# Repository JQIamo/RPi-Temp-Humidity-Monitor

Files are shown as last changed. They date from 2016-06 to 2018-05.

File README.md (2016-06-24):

# RPi-Temp-Humidity-Monitor
Raspberry-Pi driven temperature and humidity sensing via DHT22.

Short-URL: http://git.io/vRFkn

## Ordering Boards:
v1.1 Boards are orderable from OSHPark at the following links:

- [PiTempLoggerv1.1-PiSide](https://oshpark.com/shared_projects/A5WHpdao) @ $34.50 per 3 boards
- [PiTempLoggerv1.1-Sensor](https://oshpark.com/shared_projects/NIQoCTse) @ $12.00 per 3 boards

They have been prototyped on a local board-fab machine, and a first run is en-route to the JQI.

## Other needed parts:
For one sensor baord:
- 1 DHT22 [from Adafruit?](https://www.adafruit.com/product/385)
- 1 of the above PiTempLoggerv1.1-Sensor
- 1 of 1-10k 1206 SMT resistor (use a lower resistance, e.g. 1-2k, if your ethernet cable is over 15 feet)
- 1 of 100nf 1206 SMT capacitor
- 1 of ethernet jack (Man. Part No. 555164-1, TE/Amp, get from any distributor)
- 1 Ethernet cable to connect to RPi (whatever length you need)

Per pi:
- 1 of the above PiTempLoggerv1.1-PiSide
- 8 of ethernet jack (Man. Part No. 555164-1, TE/Amp, get from any distributor)
- 1 of 26-pin 2x13 header
- 1 ribbon cable, either:
  - 26 pin
  - 40 pin
  - "Downgrade" cable [from Adafruit](https://www.adafruit.com/products/1986) <-Could also be made yourself with ribbon or connector
- 1 ethernet cable for network access

## Installing on a Raspberry Pi
See instructions in `INSTALL.md`

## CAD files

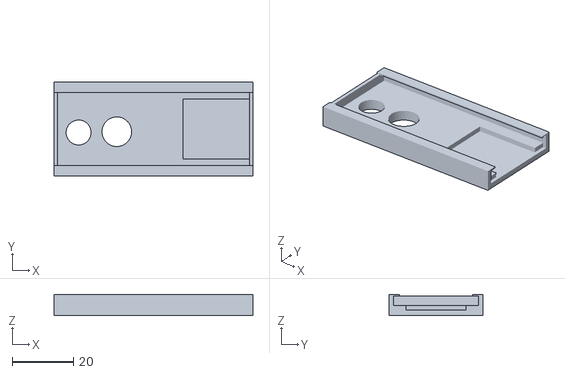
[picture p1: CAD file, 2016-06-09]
RPi-Tempmonitorcase.STL
64.8 x 30.7 x 6.86

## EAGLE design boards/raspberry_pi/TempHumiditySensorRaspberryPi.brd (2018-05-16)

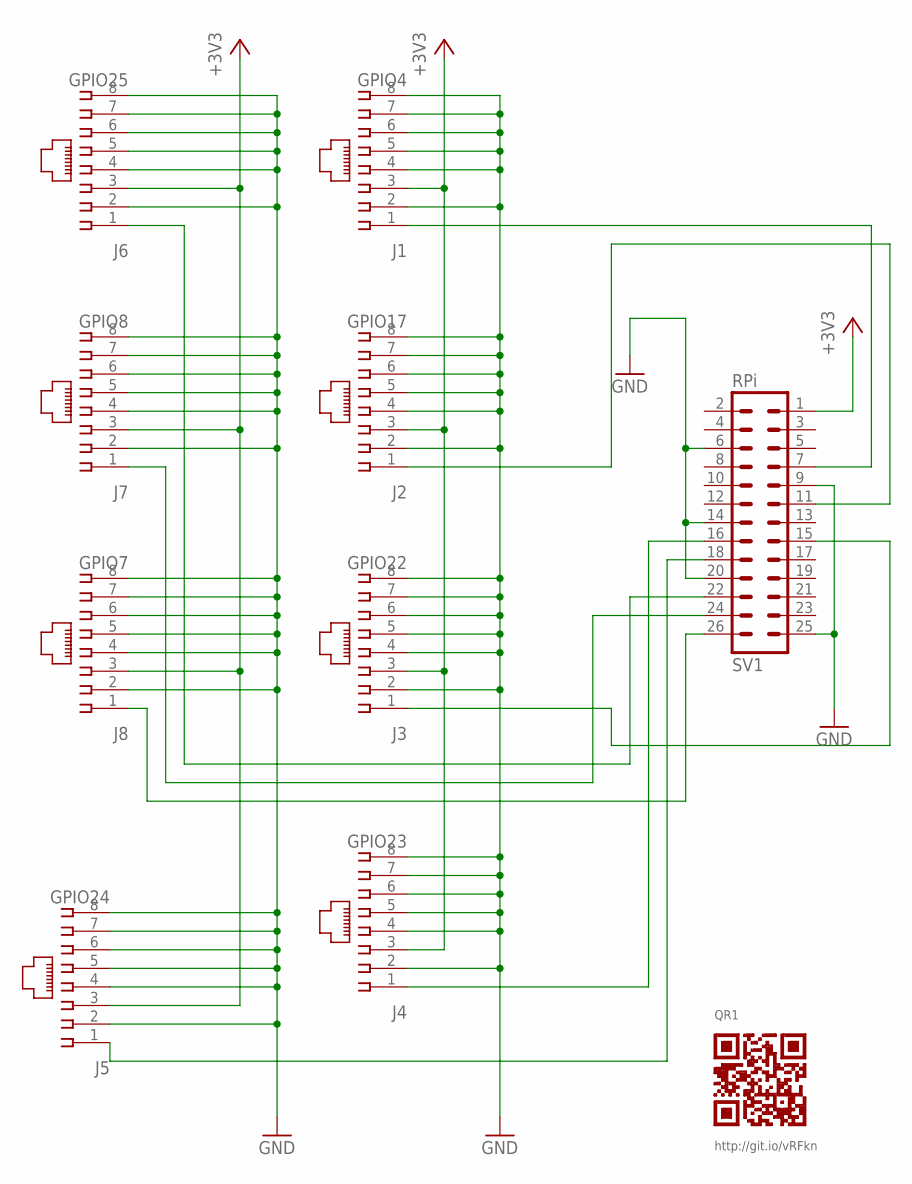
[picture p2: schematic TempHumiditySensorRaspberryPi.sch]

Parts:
J1: GPIO4; 555164-1; PARTNO 5555164-1
J2: GPIO17; 555164-1; PARTNO 5555164-1
J3: GPIO22; 555164-1; PARTNO 5555164-1
J4: GPIO23; 555164-1; PARTNO 5555164-1
J5: GPIO24; 555164-1; PARTNO 5555164-1
J6: GPIO25; 555164-1; PARTNO 5555164-1
J7: GPIO8; 555164-1; PARTNO 5555164-1
J8: GPIO7; 555164-1; PARTNO 5555164-1
QR1: QR-HTTP://GIT.IO/VRFKN
SV1: RPi; ML26; PARTNO SBH11-PBPC-D13-ST-BK

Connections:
+3V3: J1.3, J2.3, J3.3, J4.3, J5.3, J6.3, J7.3, J8.3, SV1.1
GND: J1.2, J1.4, J1.5, J1.6, J1.7, J1.8, J2.2, J2.4, J2.5, J2.6, J2.7, J2.8, J3.2, J3.4, J3.5, J3.6, J3.7, J3.8, J4.2, J4.4, J4.5, J4.6, J4.7, J4.8, J5.2, J5.4, J5.5, J5.6, J5.7, J5.8, J6.2, J6.4, J6.5, J6.6, J6.7, J6.8, J7.2, J7.4, J7.5, J7.6, J7.7, J7.8, J8.2, J8.4, J8.5, J8.6, J8.7, J8.8, SV1.6, SV1.9, SV1.14, SV1.20, SV1.25
unnamed: J1.1, SV1.7
unnamed: J8.1, SV1.26
unnamed: J2.1, SV1.11
unnamed: J3.1, SV1.15
unnamed: J4.1, SV1.16
unnamed: J6.1, SV1.22
unnamed: J7.1, SV1.24
unnamed: J5.1, SV1.18

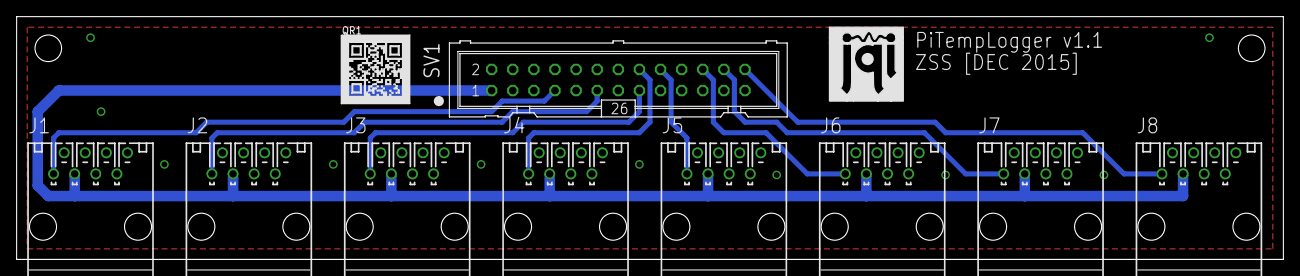
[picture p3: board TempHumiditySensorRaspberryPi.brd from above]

Board: 2 copper layers, 152.4 x 29.2 mm, 11 parts (0 on the bottom side), 10 nets.

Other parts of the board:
LOGO1: JQI-LOGOSILK; JQI_LOGO_NEGATIVE-SILKSCREEN

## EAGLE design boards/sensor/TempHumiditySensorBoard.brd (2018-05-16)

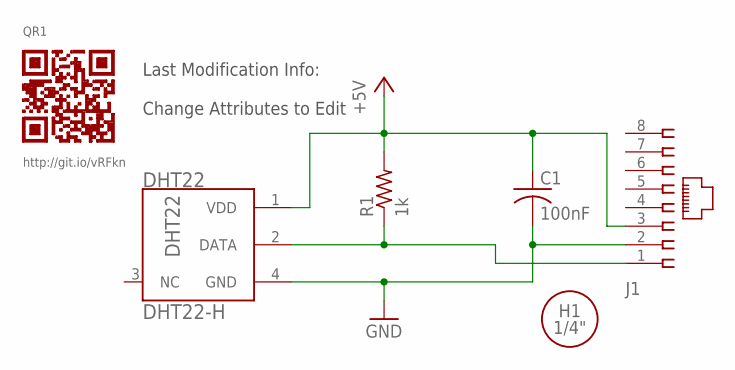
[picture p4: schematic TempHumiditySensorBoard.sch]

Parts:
C1: 100nF; C1206; PARTNO CL31B104JBCNNNC
DHT22: DHT22-H; PARTNO 385
H1: MOUNT-HOLE-1/4"-FREE
J1: 555164-1; PARTNO 555164-1
QR1: QR-HTTP://GIT.IO/VRFKN
R1: 1k; R1206; PARTNO ERJ-8ENF2001V
U$2: INFOROW; INIT_DATE_LINE

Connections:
+5V: C1.1, DHT22.1 (VDD), J1.3, R1.2
DATA: DHT22.2 (DATA), J1.1, R1.1
GND: C1.2, DHT22.4 (GND), J1.2

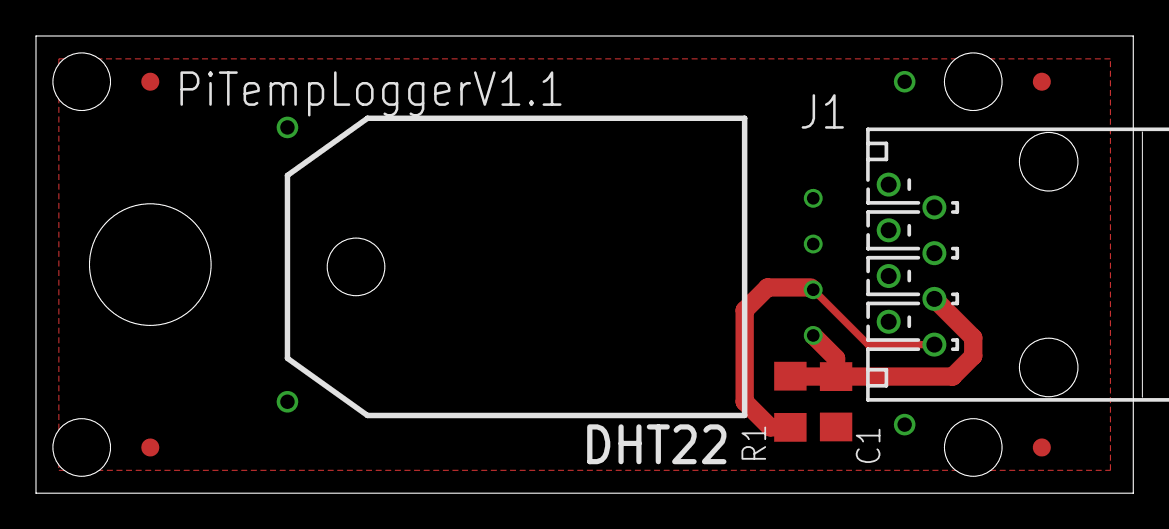
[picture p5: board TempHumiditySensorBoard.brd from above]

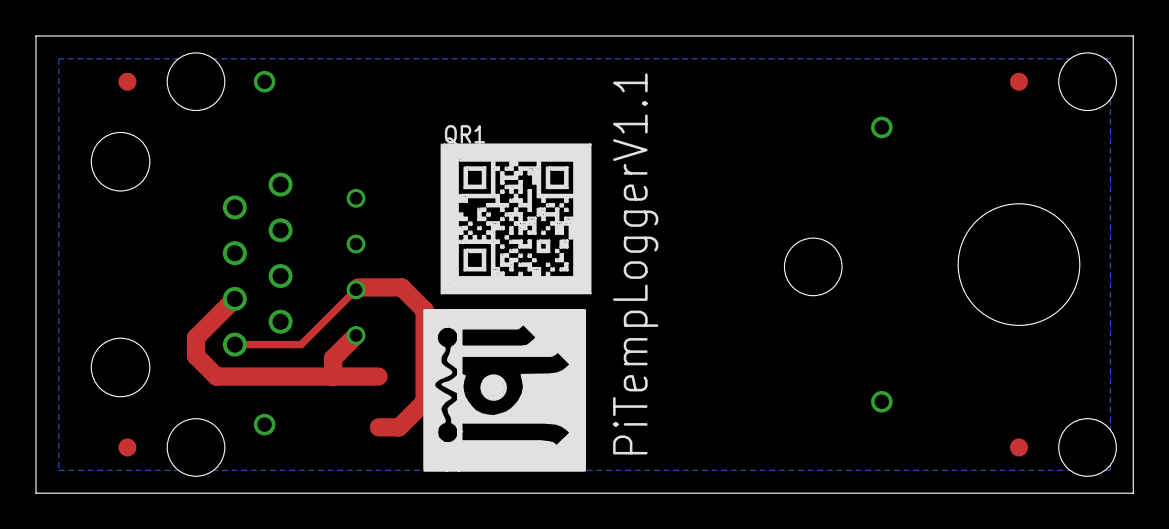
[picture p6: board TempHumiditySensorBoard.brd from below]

Board: 2 copper layers, 61.0 x 25.4 mm, 12 parts (3 on the bottom side), 3 nets.

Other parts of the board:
U$1, U$3, U$4, U$5: FID1MM
U$6: JQI_LOGO_NEGATIVE-SILKSCREEN

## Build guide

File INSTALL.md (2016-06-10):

# Installing the Scripts on Raspberry Pi #

You should have already compiled and installed the temperature sensor reading library.

You'll also need to execute most off these commands using `sudo`.

## Setup Configuration Information ##
Copy the default configuration file to the expected place, then copy it to setup our settings:

    mkdir -p /etc/templogger/
	cp templogger.conf.defaults /etc/templogger/templogger.conf.defaults
    cp /etc/templogger/templogger.conf.defaults /etc/templogger/templogger.conf

Now you'll want to edit `/etc/templogger/templogger.conf` to whichever values you'll be using.  Comments in that file (or `/etc/templogger/templogger.conf.defaults`) explain the options.

When you're finished, make sure the permissions are set to safe values.  We store passwords in the .conf, so we only want it to be readable by a user with sufficient permissions:

    chown root:root /etc/templogger/templogger.conf*
    chmod 711 /etc/templogger/templogger.conf*

## Install Dependencies

### Python-dev and Pip ###
We'll use `pip` to handle some other dependencies.  If you don't have it, or need to upgrade:

    sudo apt-get install python-pip python-dev build-essential
    sudo apt-get install --upgrade pip python-dev

### Adafruit\_Python\_DHT ###
We'll want to compile on the Raspberry Pi. We can do that in memory to speed that process up, so here's the recommended method:

1. Clone the Adafruit repository somewhere on disk:
 
    `git clone https://github.com/adafruit/Adafruit_Python_DHT.git`

2. Copy it into the shared memory space:

    `cp -r Adafruit_Python_DHT/ /dev/shm/`

3. Compile and install.

    `cd /dev/shm/Adafruit_Python_DHT`

    `sudo python setup.py install`

4. _(Optional)_ Copy compiled objects back to where you got them

    `sudo cp -r . <path_to_cloned_repository>`

5. Clean up _(Optional, will be erased at next restart)_

    `rm -rf /dev/shm/Adafruit_Python_DHT`

### InfluxDB Python Client ###

Pip should find and install dependencies for us, so you should only need to run:

    pip install influxdb
	pip upgrade influxdb

## Test Function ##

Before we install them in a repeating fashion, you should test that everything is working.  Manually run the script (will require sudo)

    ./readInfluxTemp.py

## Move Scripts ##
The nuts and bolts is handled in two script, one of which requires a little manual configuration

First, copy the scripts to their final locations and set permissions:

    cp readInfluxTemp.py /usr/local/sbin/readInfluxTemp.py
	chown root:root /usr/local/sbin/readInfluxTemp.py
	chmod 711 /usr/local/sbin/readInfluxTemp.py
    
    cp uploadMissedTemps /etc/cron.hourly/
	chown root:root /etc/cron.hourly/uploadMissedTemps.py
	chmod 711 /etc/cron.hourly/uploadMissedTemps.py

Next, setup the cron entry to run `readInfluxTemp.py` every minute. Edit the file `/etc/crontab` and 
add these lines to the end:

    ## Do influx temp logging every minute
    */1 *	* * *	root	/usr/local/sbin/readInfluxTemp.py > /dev/null

## Verify It is Working ##

To check if it is working, we'll watch the system log for an entry saying it ran the cron job. (You shouldn't need `sudo` for this

    tail -n10 -f /var/log/syslog

You should have to wait no longer than a minute for a line like

    Dec 16 13:29:01 disorderedpi /USR/SBIN/CRON[17471]: (root) CMD (/usr/local/sbin/readInfluxTemp.py > /dev/null)

to appear.  If it does, check the database you're writing to for the new points.

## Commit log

2015-12-16 Add Raspberry Pi interface board
    [TempHumiditySensorRaspberryPi.brd, TempHumiditySensorRaspberryPi.sch]
2015-12-16 Add Sensor Board
    [TempHumiditySensorBoard.brd, TempHumiditySensorBoard.sch]
2015-12-16 Add scripts to handle actual logging to influxdb
    readInfluxTemp.py:
    - Handles one-time reading of sensors
    - Attempts to post readings to an influxdb
    - If posting fails, stores to a temporary location for possible
    recovery
    uploadMissedTemps:
    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
2015-12-16 QR Code appears on schematic, has 'QR' identifier
    [TempHumiditySensorBoard.brd, TempHumiditySensorBoard.sch]
2015-12-16 Work with different board versions
    Multiple versions of the board exists that have different pin<->channel
    mappings. Added:
    - Ability to spec. board version in the configuration file
    - Ability to override pin on a channel-by-channel basis from
    configuration file
    - Default pin-maps in the sensor-reading script.
    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
2016-06-09 Add files via upload
    uploaded cad file for the plastic case used for the temp monitor
    [RPi-Tempmonitorcase.STL]
2016-06-09 Delete RPi-Tempmonitorcase.STL
    Uploading a newer version of the file
    [RPi-Tempmonitorcase.STL]
2016-06-09 CAD file for the RPi temp monitor's plastic case
    [RPi-Tempmonitorcase.STL]
2016-06-09 CAD file for the sensor board's plastic case
    [RPi-Tempmonitorcase.STL]
2016-06-24 update the resistance of the pull-up resistor
    lowering the resistance of the pull-up; the sensor with a 10k resistor does not work for distances greater than 15 feet
2018-05-16 MacroFab files and BOM
    Added BOMs for use with eagle-config and production files for MacroFab.
    DSB
    [TempHumiditySensorBoard.brd, TempHumiditySensorBoard.sch, TempHumiditySensorRaspberryPi.brd, TempHumiditySensorRaspberryPi.sch]
